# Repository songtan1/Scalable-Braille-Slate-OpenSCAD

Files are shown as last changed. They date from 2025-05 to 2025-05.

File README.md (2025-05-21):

# Scalable-Braille-Slate-OpenSCAD

This is a free software to make Braille Slate for 6 dot braille, 8 dot braille, and dot graphics with OpenSCAD.

There are two braille types - 6 dot braille (2 column * 3 row) and 8 dot braille (2 column * 4 row). The 6 dot braille has 64 (2^6) different characters and the 8 dot braille has 256 (2^8) characters. Each dot position is named as follows:

1 4

2 5

3 6

7 8

The braille specification defines its size with 5 % tolerance. There are three types in use - Basic, Compressed (95%), and Jumbo dot (125%). Basic uses 1.6 mm dot with 2.4 mm dot spacing. The 95% compressed one is commonly used for reading materials. The cell spacing is further reduced to put more characters in a line. Jumbo dot uses the same basic dot size with 125% dot spacing. It is used for the signage, etc., with the consideration of people with less dexterity.

Type ________ Basic Compressed Jumbo Remark

Scale _______ 1.0 0.95 1.25

Dot Size ____ 1.6 1.5 1.6

Dot-X Spacing 2.4 2.3 3.1 Range: 2.3-2.5

Dot-Y Spacing 2.4 2.3 3.1 Range: 2.3-2.5

Dot Height __ - 0.6 - Minimum (Range: 0.6-0.9)

Cell Spacing 6.0 5.5 - Minimum (Range: 5.5-7.5)

Line Spacing 11 10 - Minimum (Range: 10-)

Cell Gap ____ 1.0 0.9 - Derived from cell spacing

Line Gap ____ 3.5 3.1 - Derived from line spacing

In the program, the initial X size is set same as the letter size paper even it is changeable. The Y size is divided into the repeat for the fast 3d rendering. One repeat has 20 dot rows and about 50 mm. One repeat is 5 lines of 6 dot braille (3 dot row with 1 spacing) or 4 lines of 8 dot braille (4 dot row with 1 spacing). I suggest to make the bottom slate with 6 repeats (300 mm) with the 1 repeat top slate (50mm) and use the bottom slate as a backboard while moving around the top slate over as needed. You may also make the slate size same as a memo pad or a name card to take a quick short note.

The font size of normal inked text is 10 to 12 points. The braille character is 24 points. The braille text takes about 200 to 240 % more space than the inked text. In the compressed braille text, the cell gap is smaller than the dot-x spacing and the line gap is bigger than the dot-y spacing for better readability while having more characters in a line.

However, if the cell gap was same as the dot-x spacing and the line gap was same as the dot-y spacing, the bottom slate would be same for 6 dot or 8 dot brailles and even could be used for the dot graphics. For this in mind, I added dots on spacing area for the bottom slate and 2nd paper holes on the top slate to assist to access most dots. The program is also designed to make a cell with any number of column and row. A cell with 5 column * 7 row with 50% scale can be used for the dotted alphabet text. It takes about the same space as the 6 dot braille.

Interestingly, the braille specification is very similar to that of LEGO(R). Lego uses the 1.6 mm unit for its brick sizes and its dot size is 3 units instead of 1.

For the fast 3d rendering, run the code on the OpenSCAD Developer Snapshot version using Manifold and turn off Automatic Preview from Customizer.

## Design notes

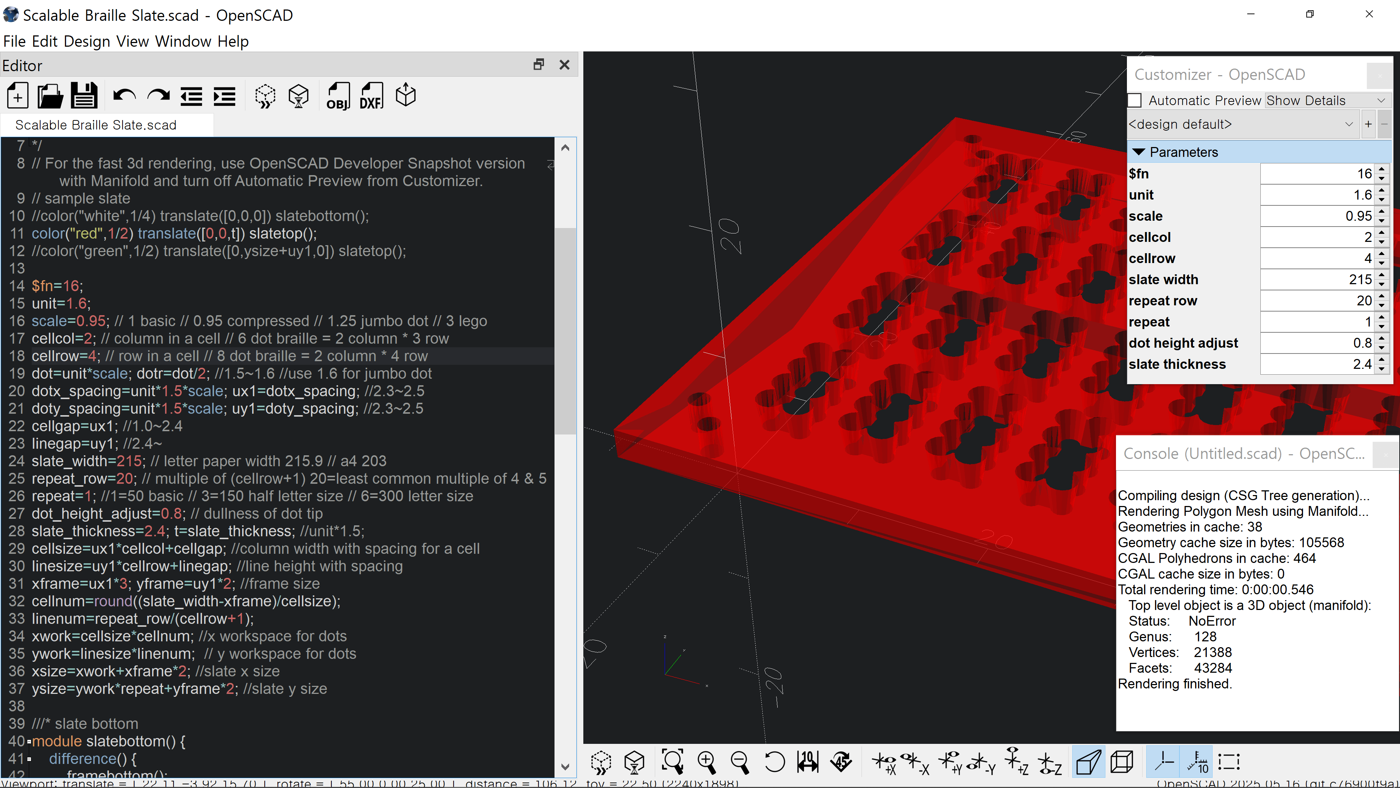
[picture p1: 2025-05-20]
Slate Top 8dot.png

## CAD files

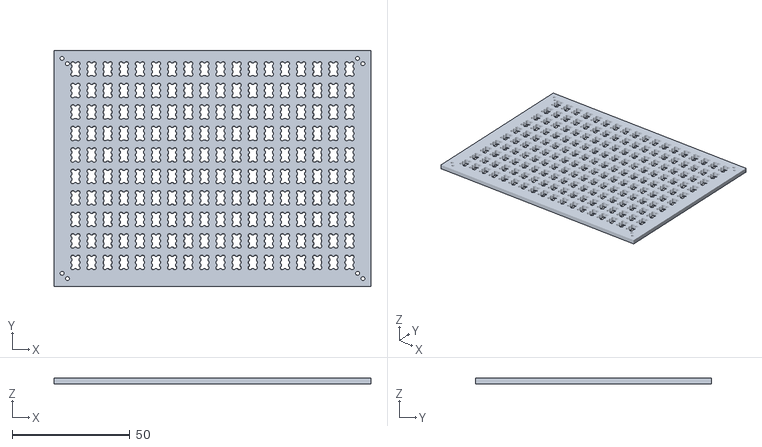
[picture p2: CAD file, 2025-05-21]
Slate Top 6dot Memopad 139x108.stl
134.5 x 100.3 x 2.40

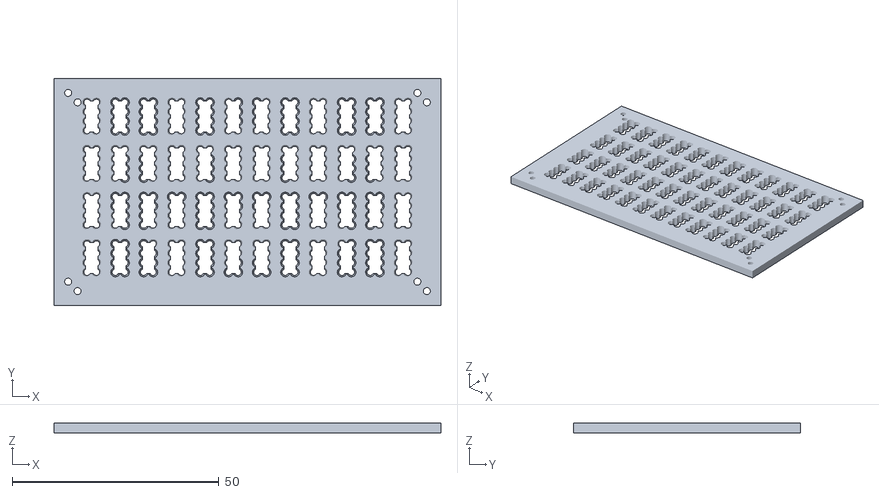
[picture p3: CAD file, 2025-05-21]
Slate Top 8dot Namecard 90x50.stl
93.5 x 54.7 x 2.40

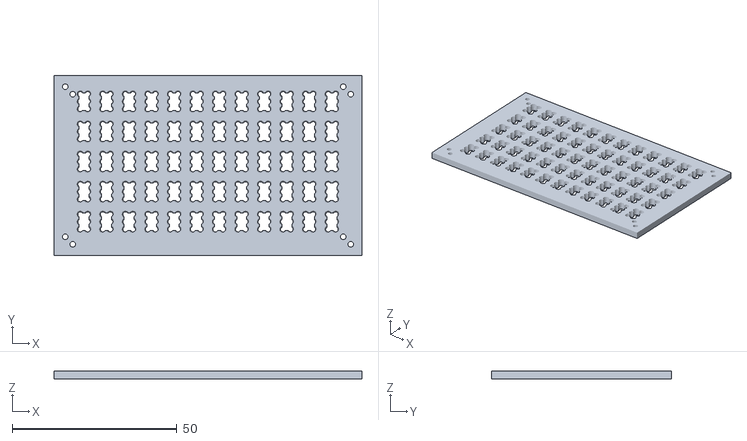
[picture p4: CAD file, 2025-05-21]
Slate Top 6dot Namecard 90x50.stl
93.5 x 54.7 x 2.40

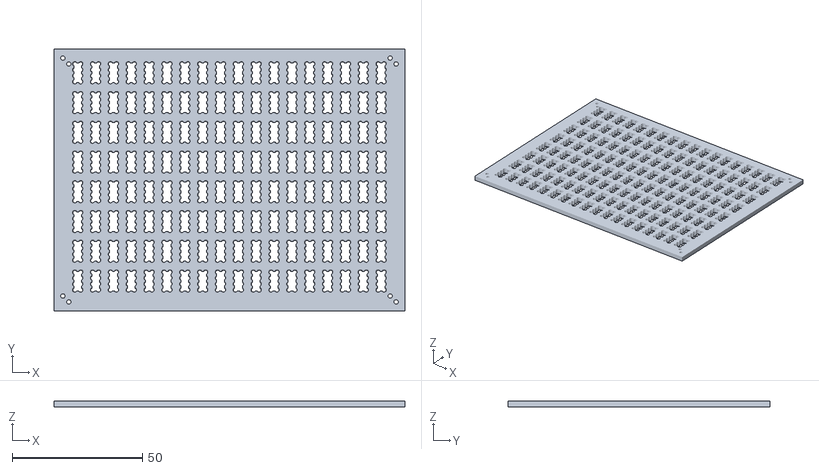
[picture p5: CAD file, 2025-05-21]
Slate Top 8dot Memopad 139x108.stl
134.5 x 100.3 x 2.40

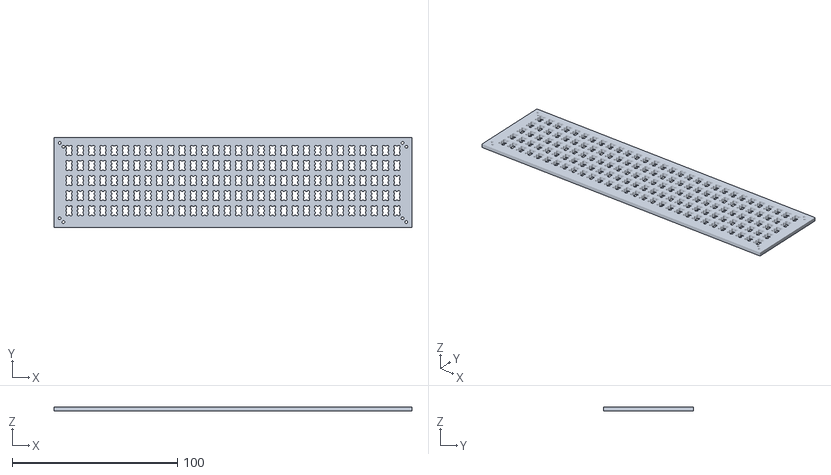
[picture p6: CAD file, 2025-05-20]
Slate Top 6dot.stl
216.6 x 54.7 x 2.40

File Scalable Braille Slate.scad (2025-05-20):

/* Scalable Braille Slate for 6 dot braille, 8 dot braille and dot graphics
Copyright (C) 2025 Jaewon Kim
LICENSE: GPL-3.0-or-later
This program is free software: you can redistribute it and/or modify it under the terms of the GNU General Public License as published by the Free Software Foundation, version 3.
This program is distributed in the hope that it will be useful, but WITHOUT ANY WARRANTY; without even the implied warranty of MERCHANTABILITY or FITNESS FOR A PARTICULAR PURPOSE. See the GNU General Public License for more details.
You should have received a copy of the GNU General Public License along with this program. If not, see <https://www.gnu.org/licenses/>.
*/
// For the fast 3d rendering, use OpenSCAD Developer Snapshot version with Manifold and turn off Automatic Preview from Customizer.
// sample slate
//color("white",1/4) translate([0,0,0]) slatebottom();
color("red",1/2) translate([0,0,t]) slatetop();
//color("green",1/2) translate([0,ysize+uy1,0]) slatetop();

$fn=16;
unit=1.6;
scale=0.95; // 1 basic // 0.95 compressed // 1.25 jumbo dot // 3 lego
cellcol=2; // column in a cell // 6 dot braille = 2 column * 3 row
cellrow=4; // row in a cell // 8 dot braille = 2 column * 4 row
dot=unit*scale; dotr=dot/2; //1.5~1.6 //use 1.6 for jumbo dot
dotx_spacing=unit*1.5*scale; ux1=dotx_spacing; //2.3~2.5
doty_spacing=unit*1.5*scale; uy1=doty_spacing; //2.3~2.5
cellgap=ux1; //1.0~2.4
linegap=uy1; //2.4~
slate_width=215; // letter paper width 215.9 // a4 203
repeat_row=20; // multiple of (cellrow+1) 20=least common multiple of 4 & 5
repeat=1; //1=50 basic // 3=150 half letter size // 6=300 letter size
dot_height_adjust=0.8; // dullness of dot tip
slate_thickness=2.4; t=slate_thickness; //unit*1.5;
cellsize=ux1*cellcol+cellgap; //column width with spacing for a cell
linesize=uy1*cellrow+linegap; //line height with spacing
xframe=ux1*3; yframe=uy1*2; //frame size
cellnum=round((slate_width-xframe)/cellsize);
linenum=repeat_row/(cellrow+1);
xwork=cellsize*cellnum; //x workspace for dots
ywork=linesize*linenum;  // y workspace for dots
xsize=xwork+xframe*2; //slate x size 
ysize=ywork*repeat+yframe*2; //slate y size

///* slate bottom
module slatebottom() {
    difference() {
        framebottom();
        for (rpt=[0:repeat-1]) {
            translate([ux1/2,rpt*ywork+uy1/2,t]) bottomcut();}}}
module framebottom() {
    translate([-xframe,-yframe,0]) cube([xsize-ux1,ysize,t]);
    for (rpt=[0:repeat-1]) {
        translate([-ux1/2,ywork*rpt,t]) paperhole(t/2,dotr,dotr);
        translate([-ux1/2,ywork*rpt,t*1.5]) paperhole(t/2,dotr,dotr/8);}}
module paperhole(t1,r1,r2) {
    x0=0; y0=-uy1/2; x1=xwork+ux1; y1=ywork-uy1/2;
    translate([x0,y0,0]) cylinder(t1,r1,r2);
    translate([x0,y1,0]) cylinder(t1,r1,r2);
    translate([x1,y0,0]) cylinder(t1,r1,r2);
    translate([x1,y1,0]) cylinder(t1,r1,r2);}
module bottomcut() {
    if (cellgap==ux1 && linegap==uy1)
        for (c1=[0:cellnum-1]) { for(l1=[0:linenum-1]) {
        translate([c1*cellsize,l1*linesize,0]) bottomcellall();}}
    else
        for (c1=[0:cellnum-1]) { for(l1=[0:linenum-1]) {
        translate([c1*cellsize,l1*linesize+linegap,0]) bottomcell();}}}
module bottomcell() {
    for (c1=[0:cellcol-1]) { for(r1=[0:cellrow-1]) {
    translate([c1*ux1,r1*uy1,0]) onedot();}}}
module bottomcellall() {
    for (c1=[0:cellcol]) { for(r1=[0:cellrow]) {
    translate([c1*ux1,r1*uy1,0]) onedot();}}}
module onedot() {
    translate([0,0,-0.1]) cylinder(0.1,dotr,dotr*1.1);
    scale([1,1,dot_height_adjust]) sphere(dotr);}
//*/
///* slate top
module slatetop() {
    difference() { frametop(); frametopcut();}
    for (rpt=[0:repeat-1]) { difference() {
        translate([0,rpt*ywork,0]) cube([xwork-cellgap,ywork,t]);
        translate([ux1/2,rpt*ywork+uy1*1.5,0]) topcut();}}}
module frametop() {
    difference() {
        translate([-xframe,-yframe,0]) cube([xsize-ux1,ysize,t]);
        translate([0,0,-0.1]) cube([xwork-cellgap,ywork*repeat,t+0.2]);}}
module frametopcut() {
    for (rpt=[0:repeat-1]) {
        translate([-ux1/2,rpt*ywork,-0.1]) paperhole(t+0.2,dotr+0.1,dotr+0.1);
        if (cellgap==ux1 && linegap==uy1)
            translate([-ux1*1.5,rpt*ywork+uy1,-0.1])
            paperhole(t+0.2,dotr+0.1, dotr+0.1);}}
module topcut() {
    for (c1=[0:cellnum-1]) { for(l1=[0:linenum-1]) {
    translate([c1*cellsize,l1*linesize+linegap,0]) topcell();}}}
module topcell() {
    translate([-ux1*0.15,-uy1*1.15,-0.1]) cube([ux1*(cellcol-0.7),uy1*(cellrow-0.7),t+0.2]);
    for (c1=[0:cellcol-1]) { for(r1=[0:cellrow-1]) {
        translate([c1*ux1,(r1-1)*uy1,-0.1]) cylinder(t+0.2,dotr,uy1/2);}}}
//*/

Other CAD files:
Slate Top 8dot.stl
